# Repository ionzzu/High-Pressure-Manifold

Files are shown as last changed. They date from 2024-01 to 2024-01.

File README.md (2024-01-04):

# High Pressure Manifold

Development of a high pressure manifold to house a miniature VYSZion battery cell at the center.

## Constraints

- Operable to temperatures of 650-800°C and pressures of 10 bar
- Manifold has two inlets and outlets, one each for gas and air
- Design for insertion of temperature probes, pressure sensors, and electrical wires

## Research Paper

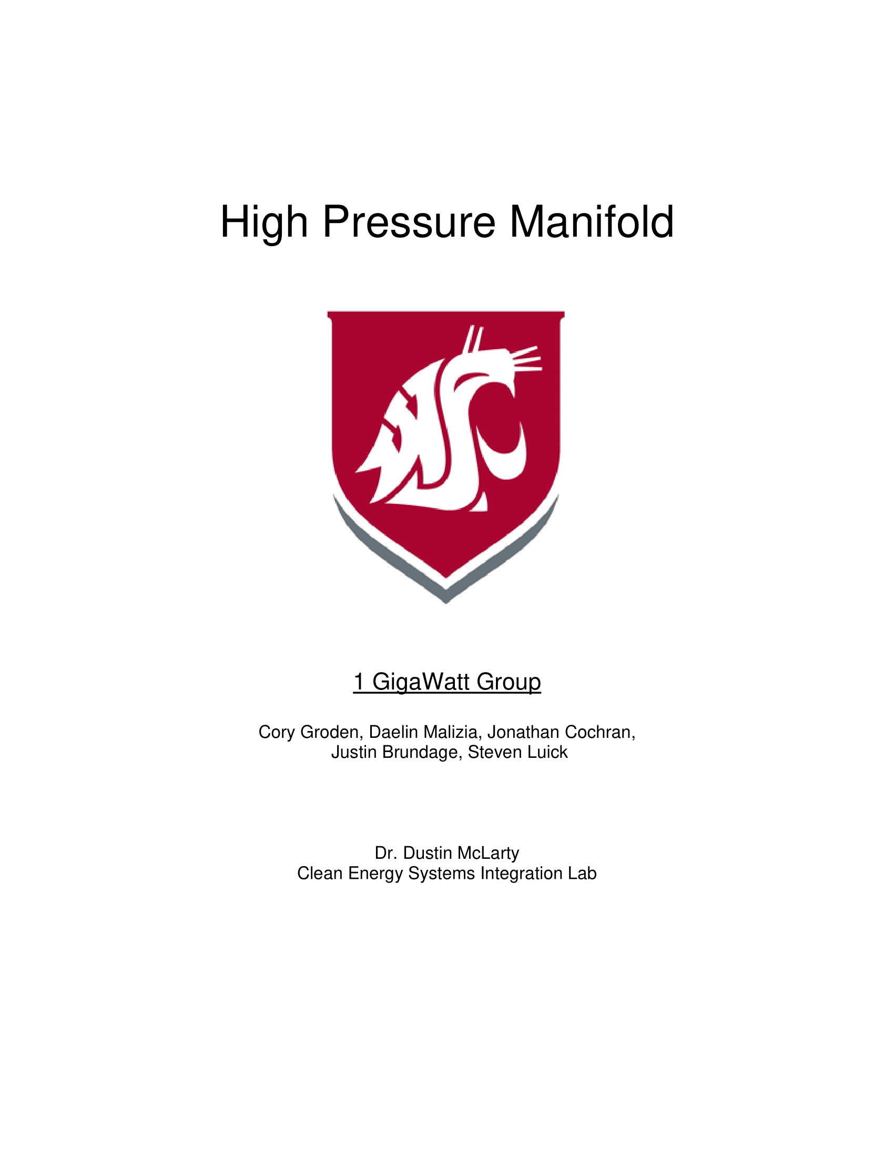
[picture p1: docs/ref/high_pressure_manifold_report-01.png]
report-01


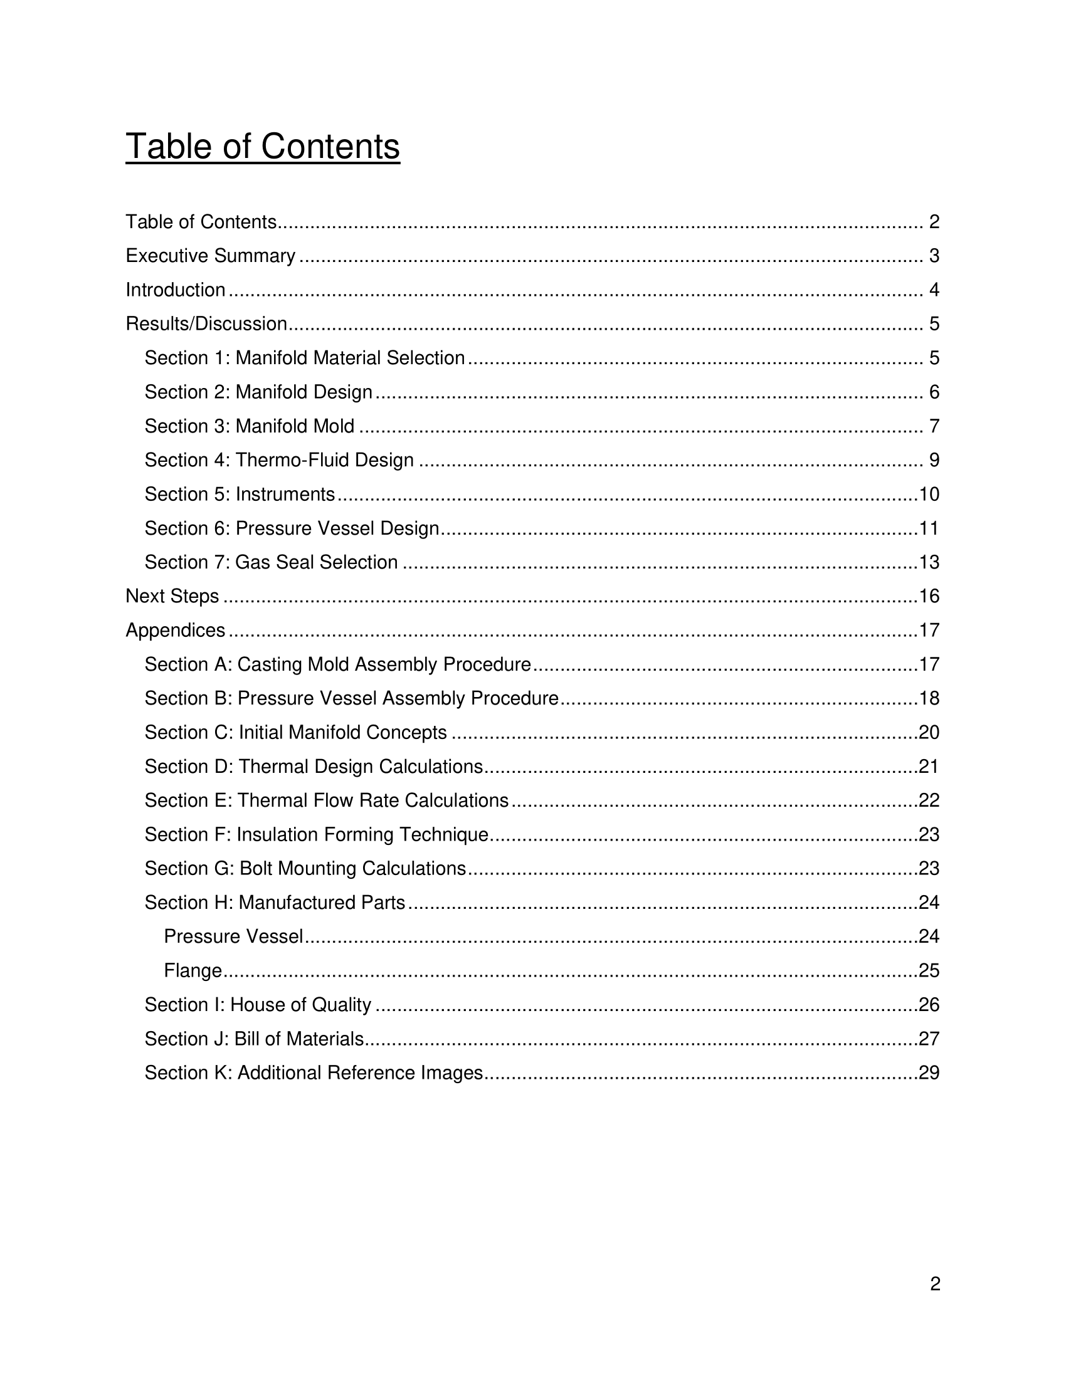
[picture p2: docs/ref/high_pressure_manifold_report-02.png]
report-02


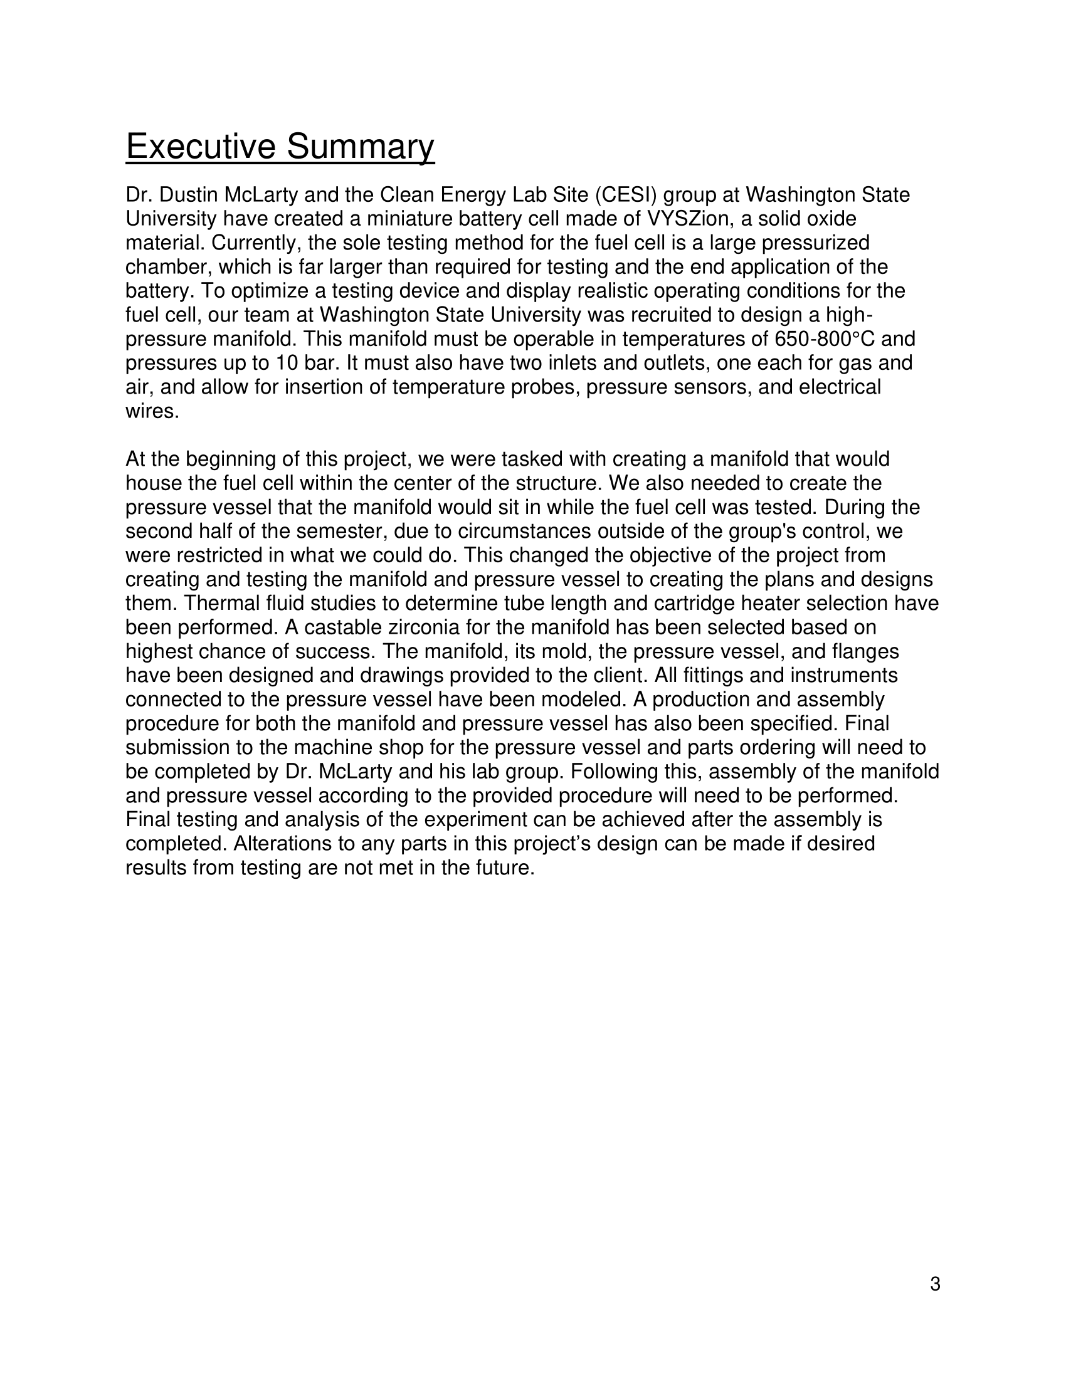
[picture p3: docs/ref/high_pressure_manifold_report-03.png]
report-03


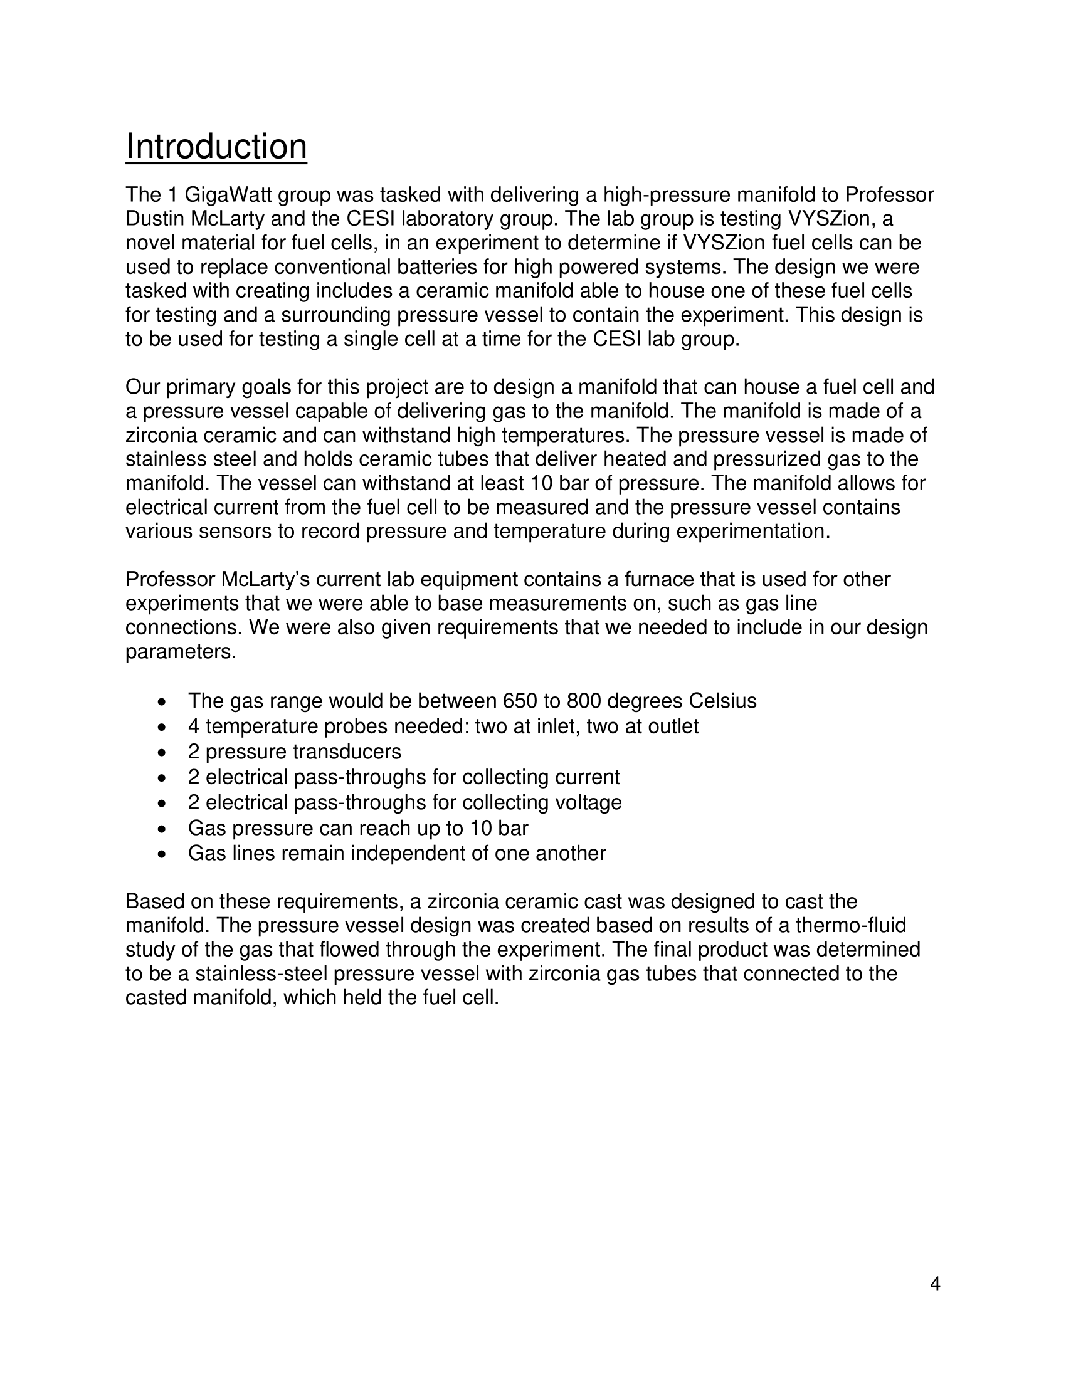
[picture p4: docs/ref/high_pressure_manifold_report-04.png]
report-04


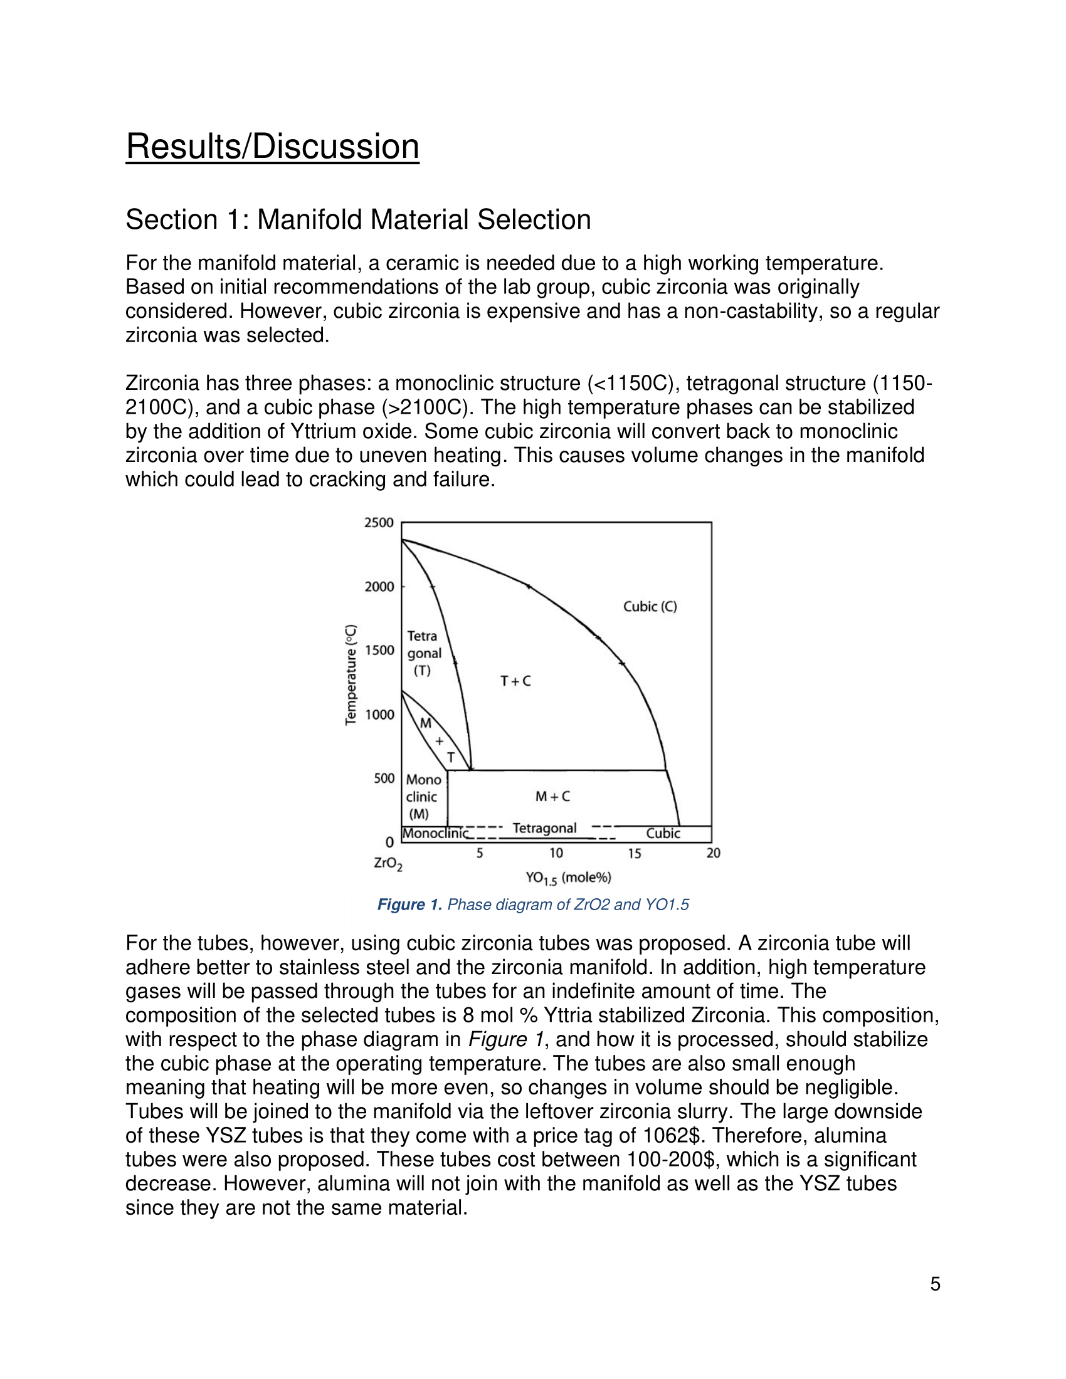
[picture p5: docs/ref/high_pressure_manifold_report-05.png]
report-05


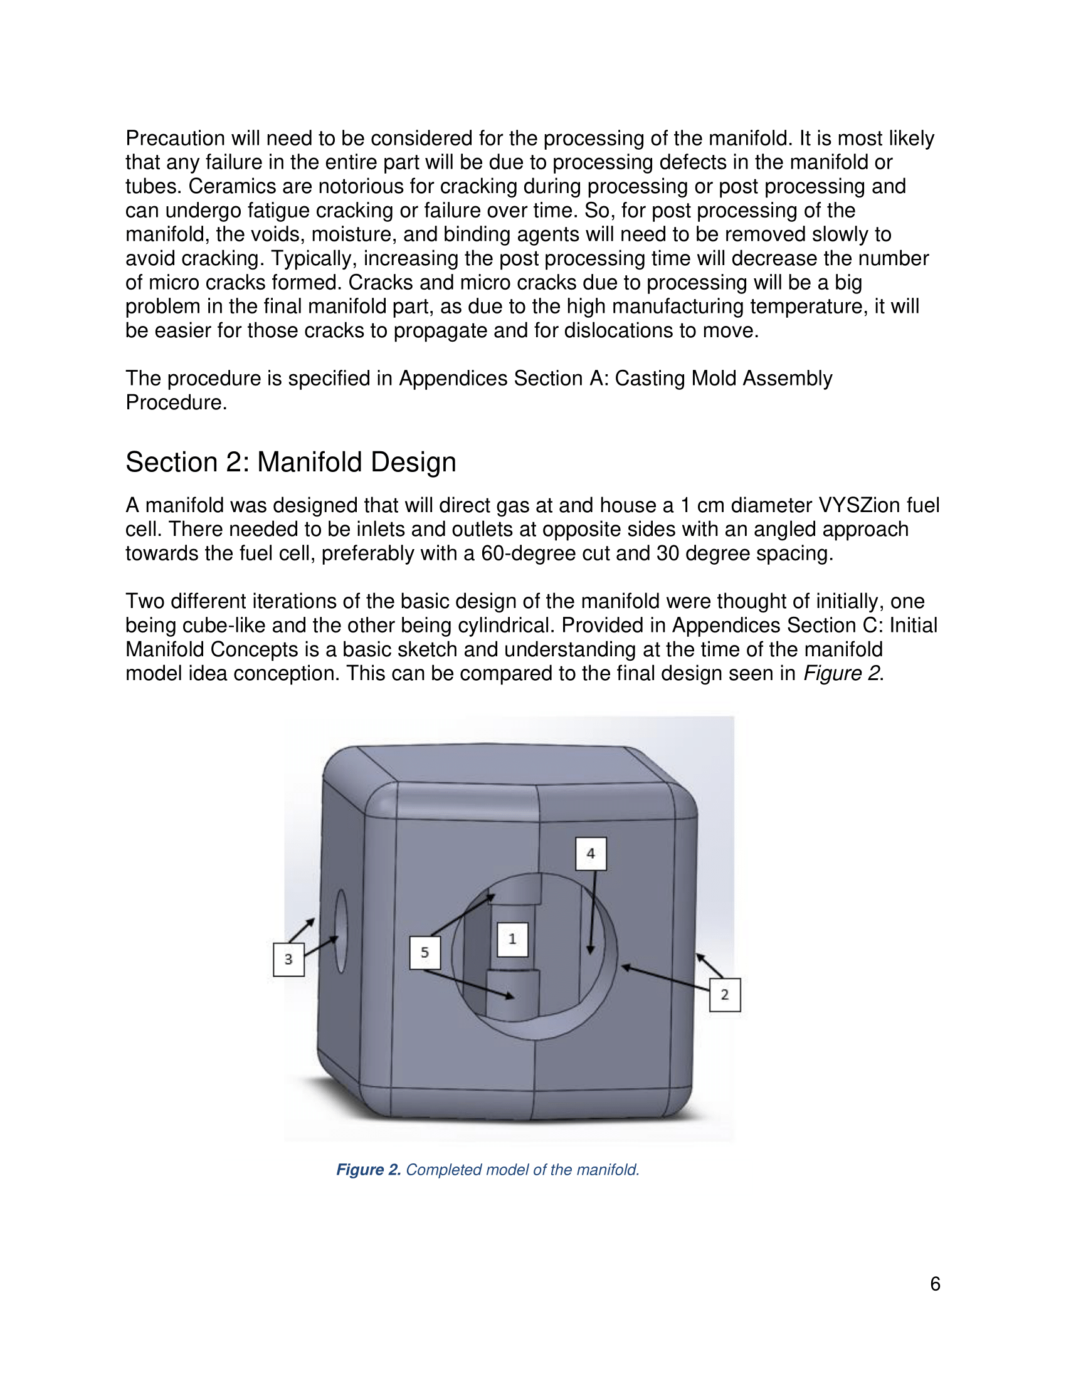
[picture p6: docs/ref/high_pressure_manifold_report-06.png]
report-06


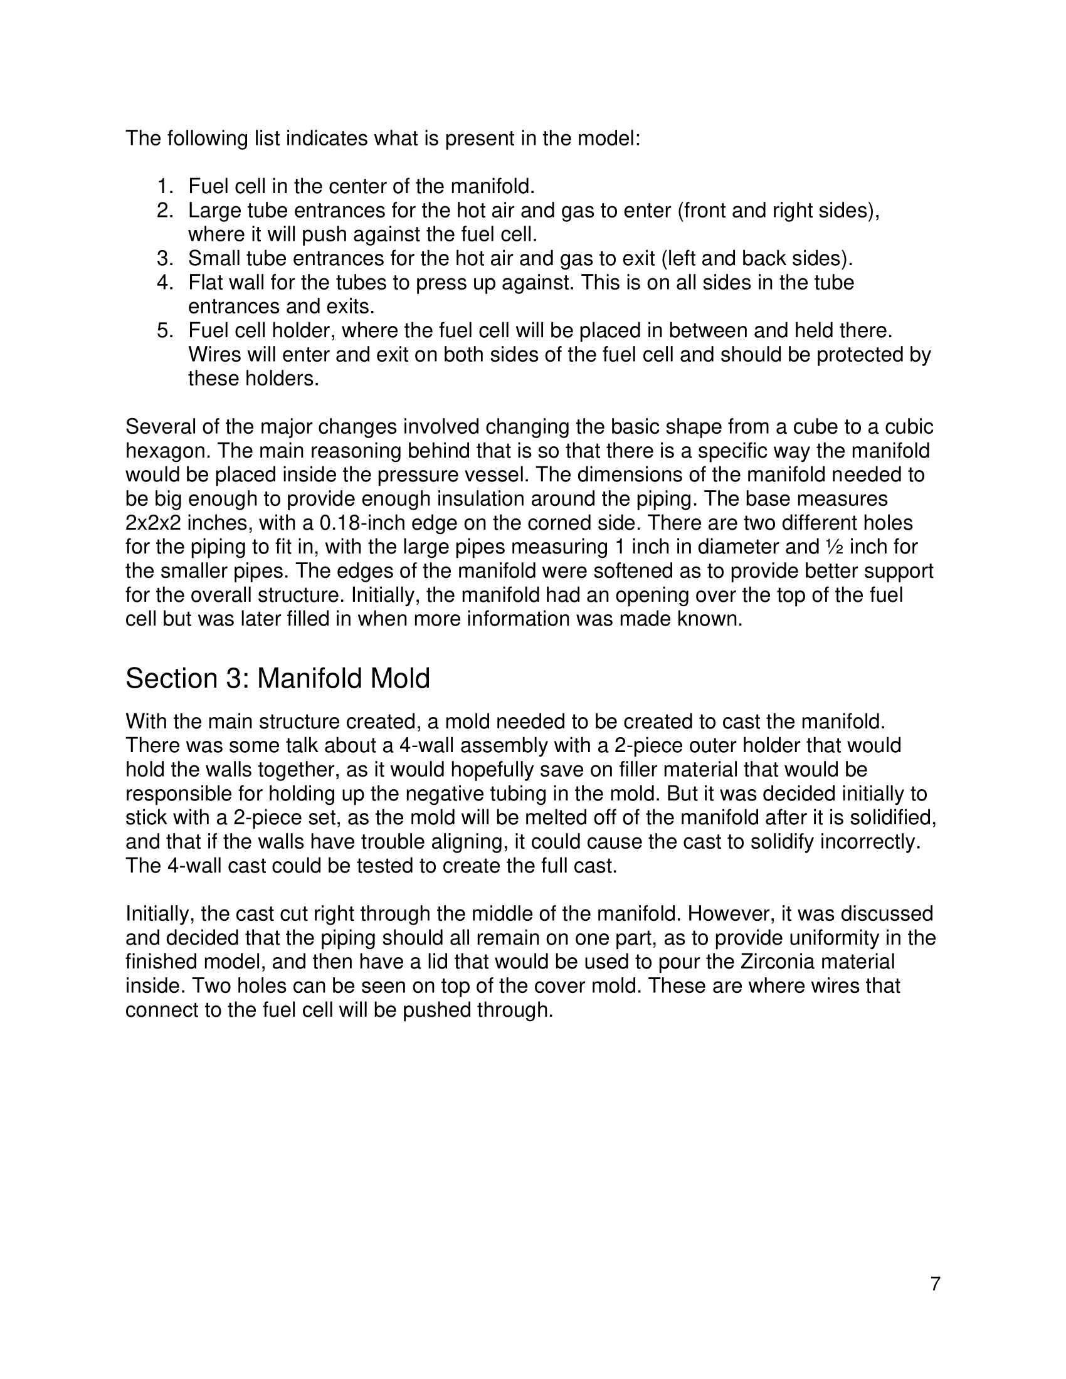
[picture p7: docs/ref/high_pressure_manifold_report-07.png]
report-07


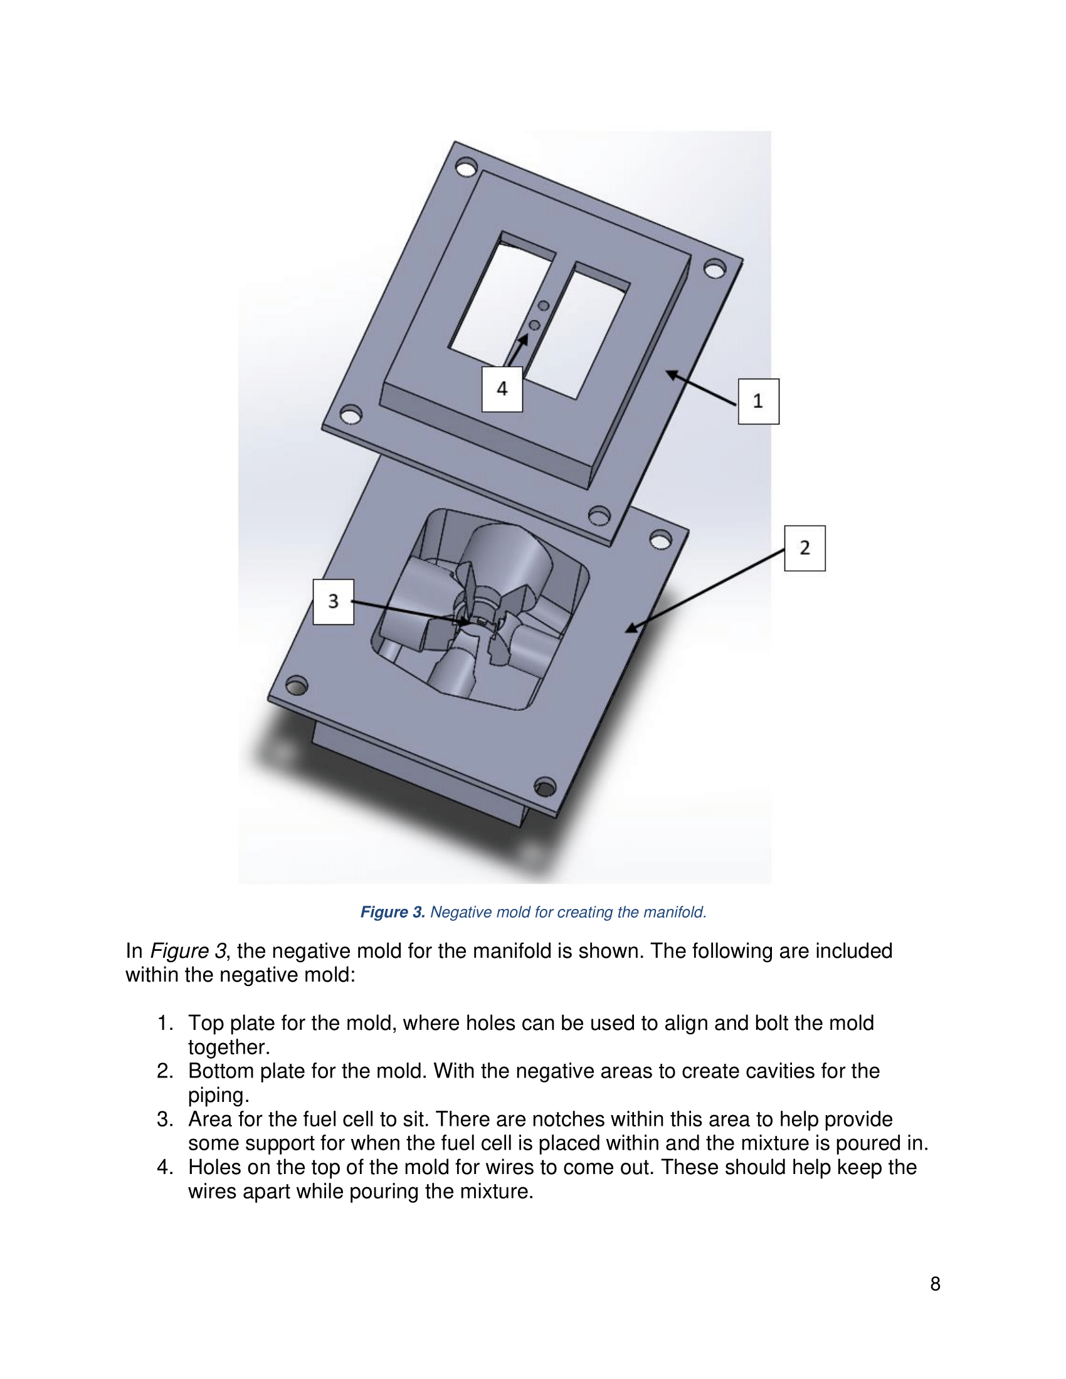
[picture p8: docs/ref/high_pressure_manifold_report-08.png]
report-08


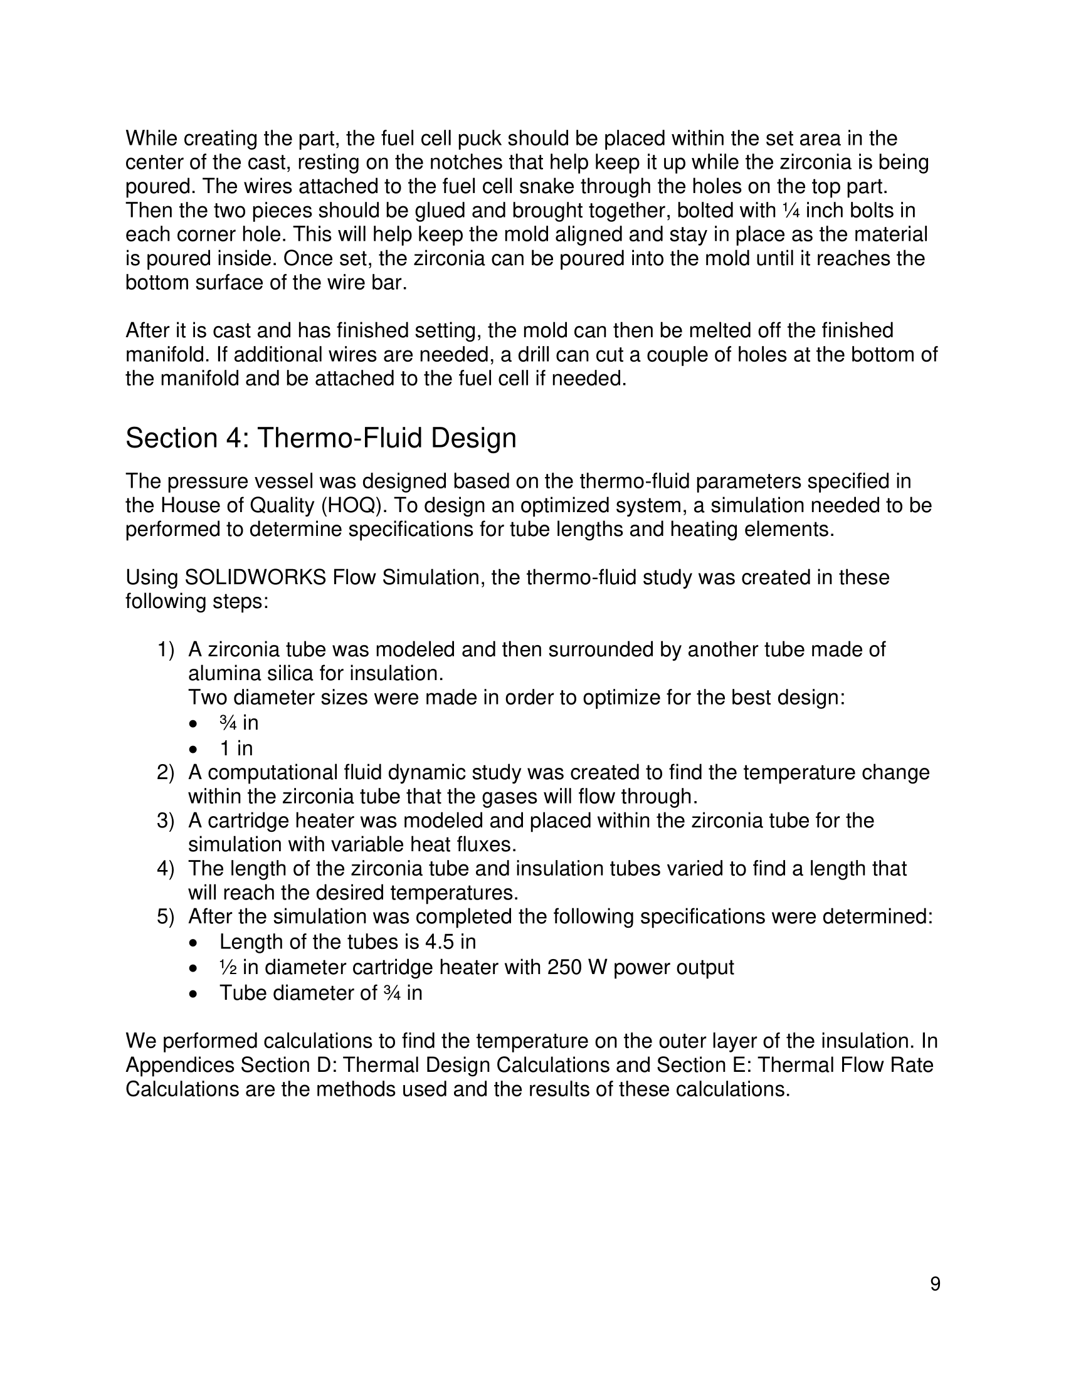
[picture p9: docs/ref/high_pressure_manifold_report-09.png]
report-09


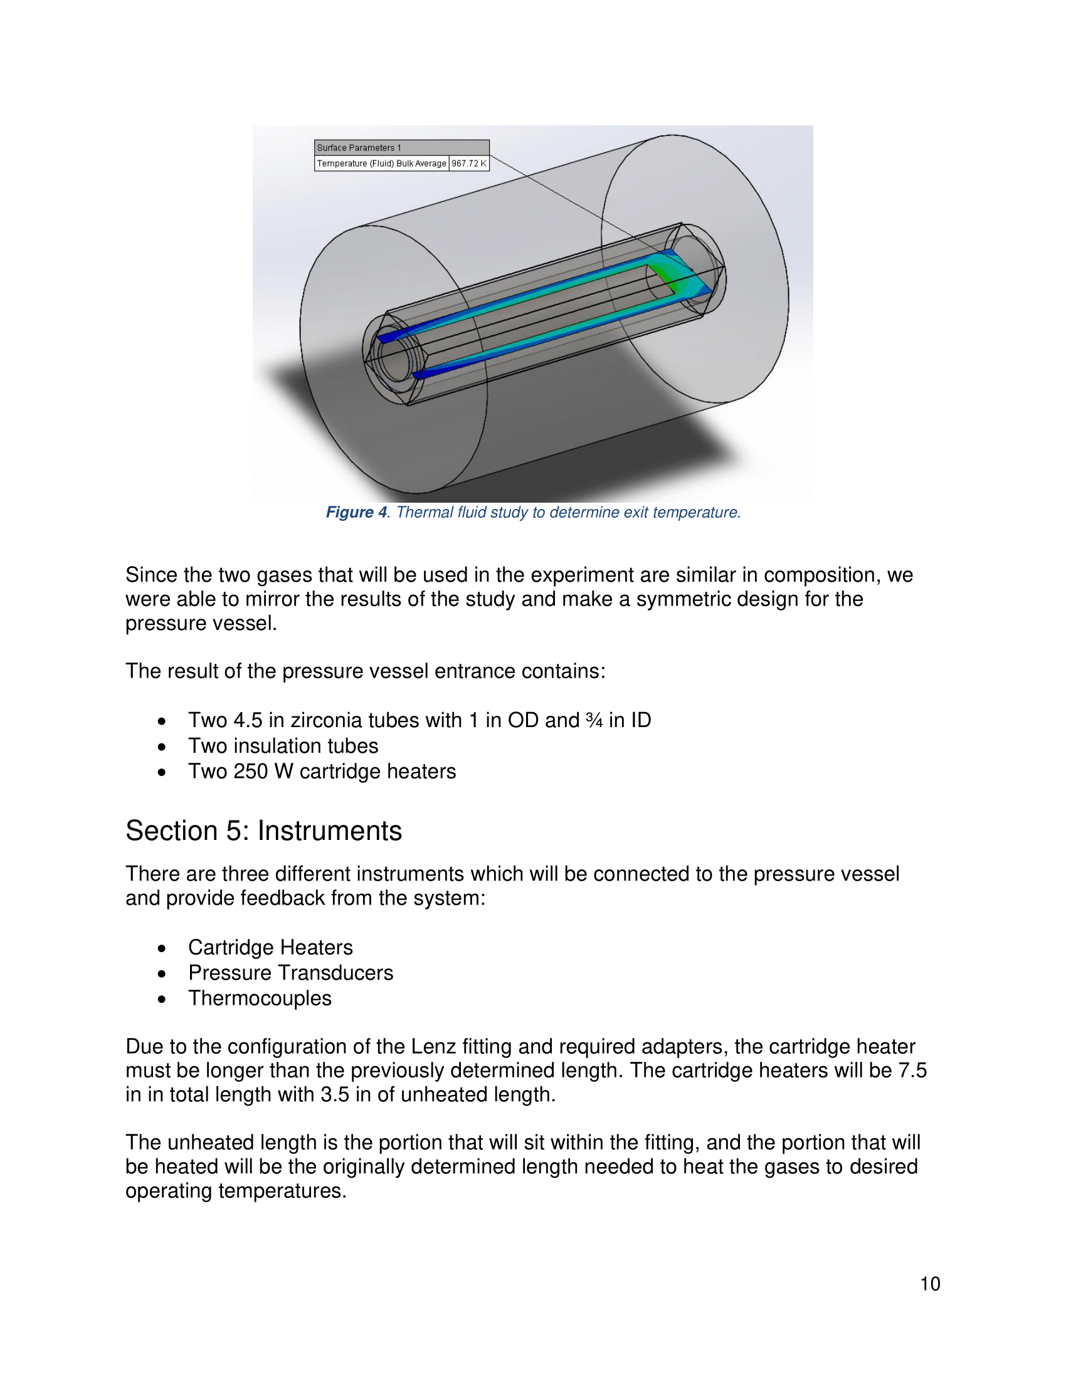
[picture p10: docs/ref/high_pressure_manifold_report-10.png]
report-10


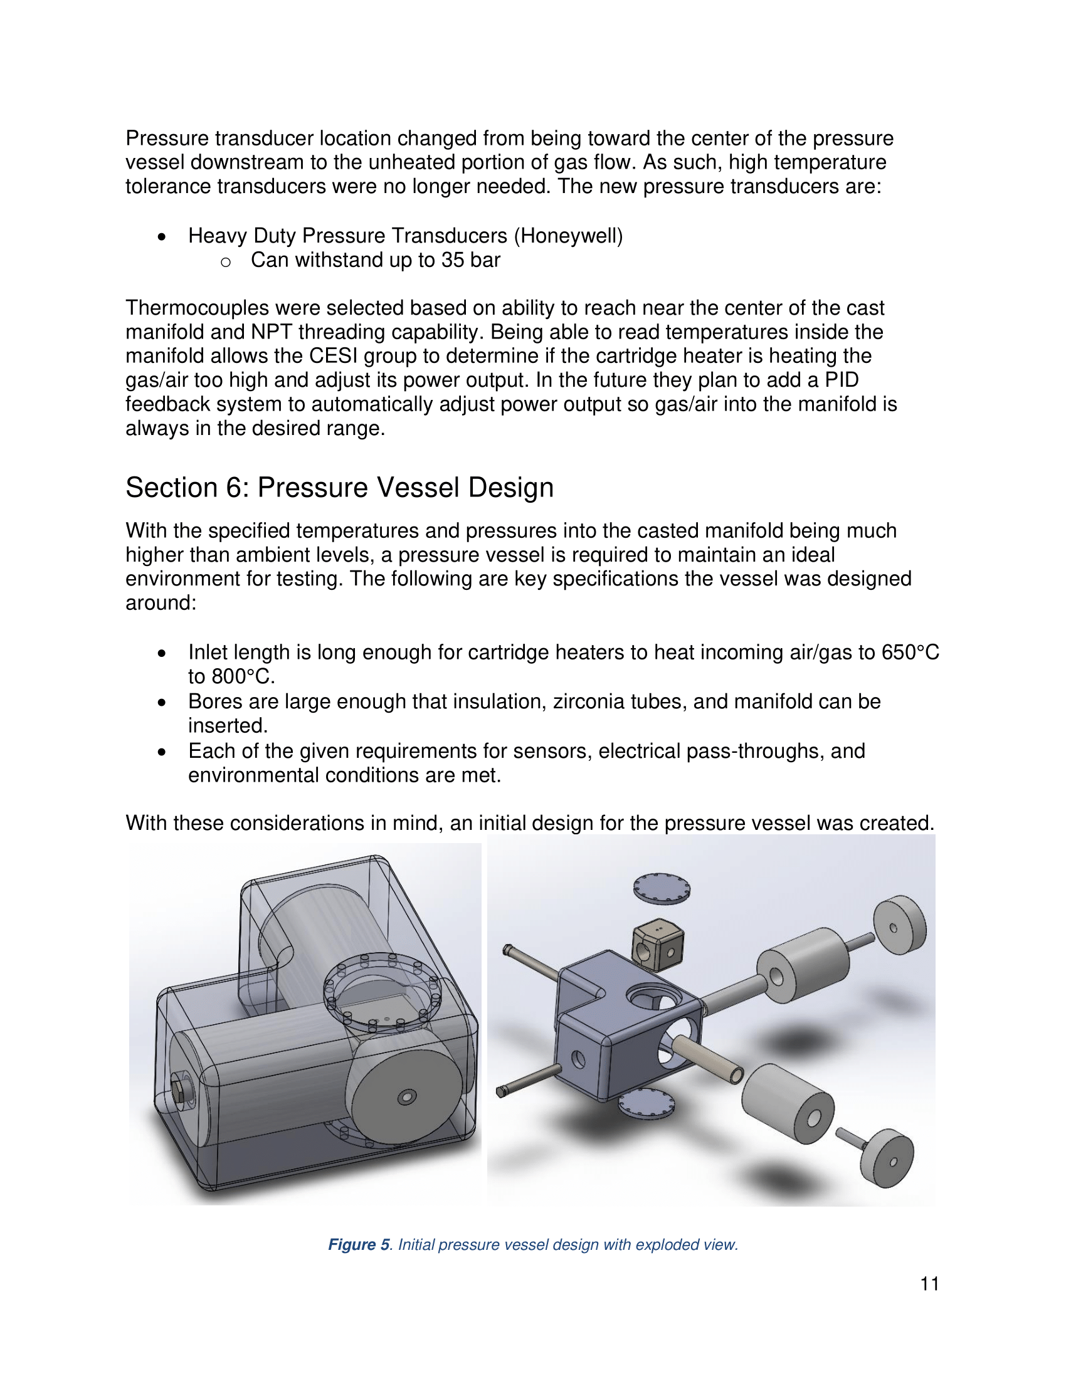
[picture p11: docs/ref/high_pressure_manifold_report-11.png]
report-11


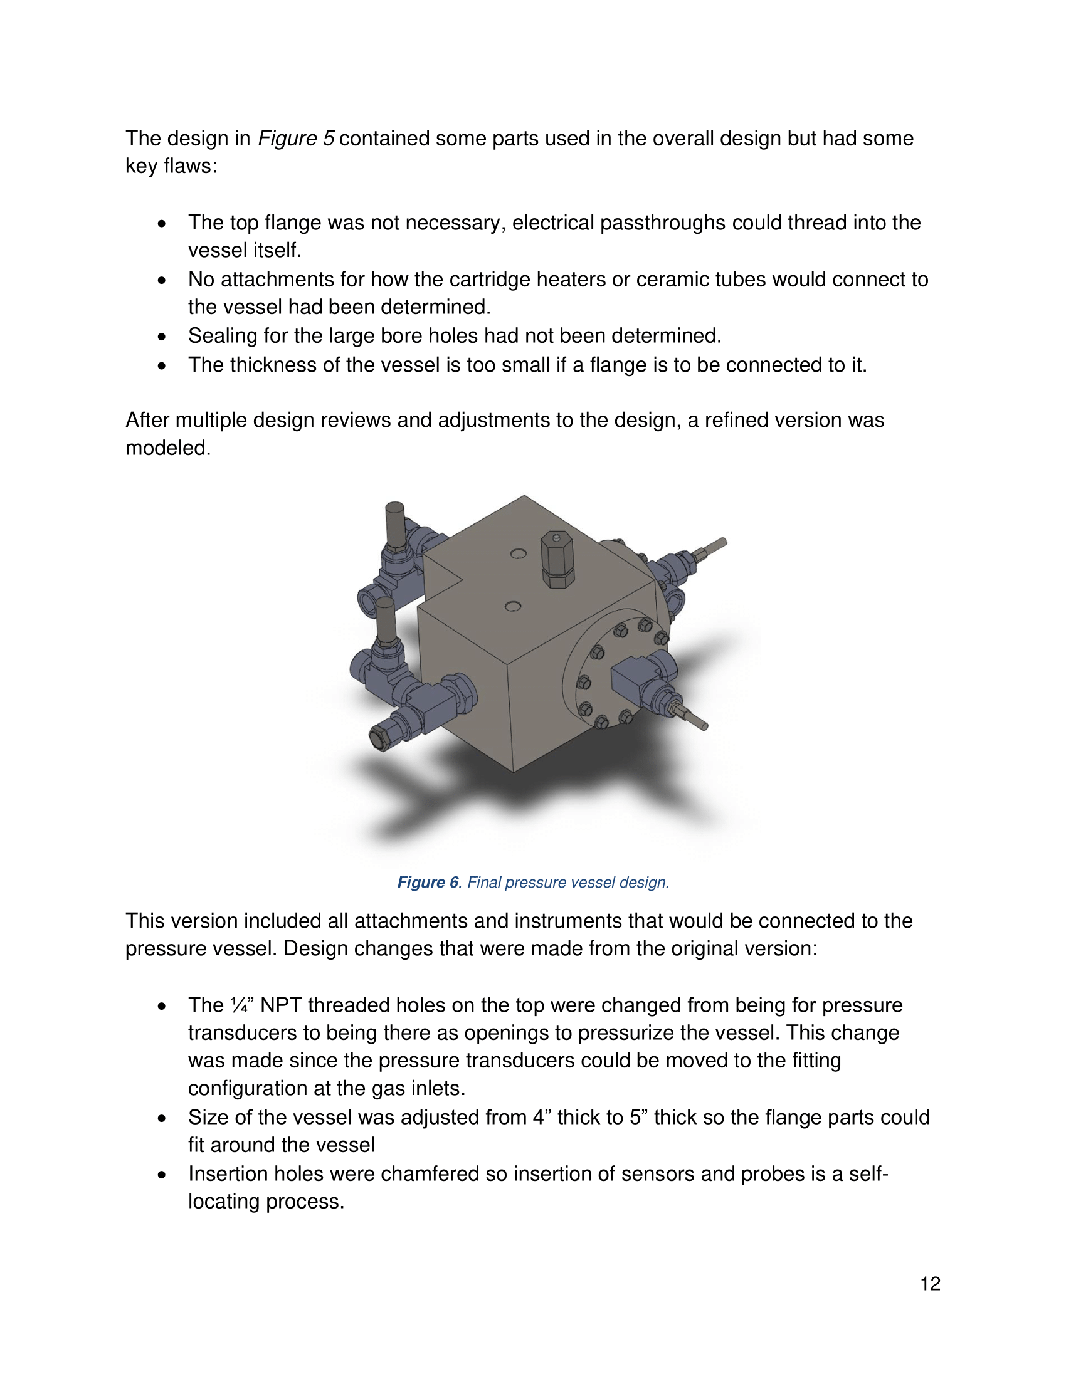
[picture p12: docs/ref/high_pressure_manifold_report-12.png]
report-12


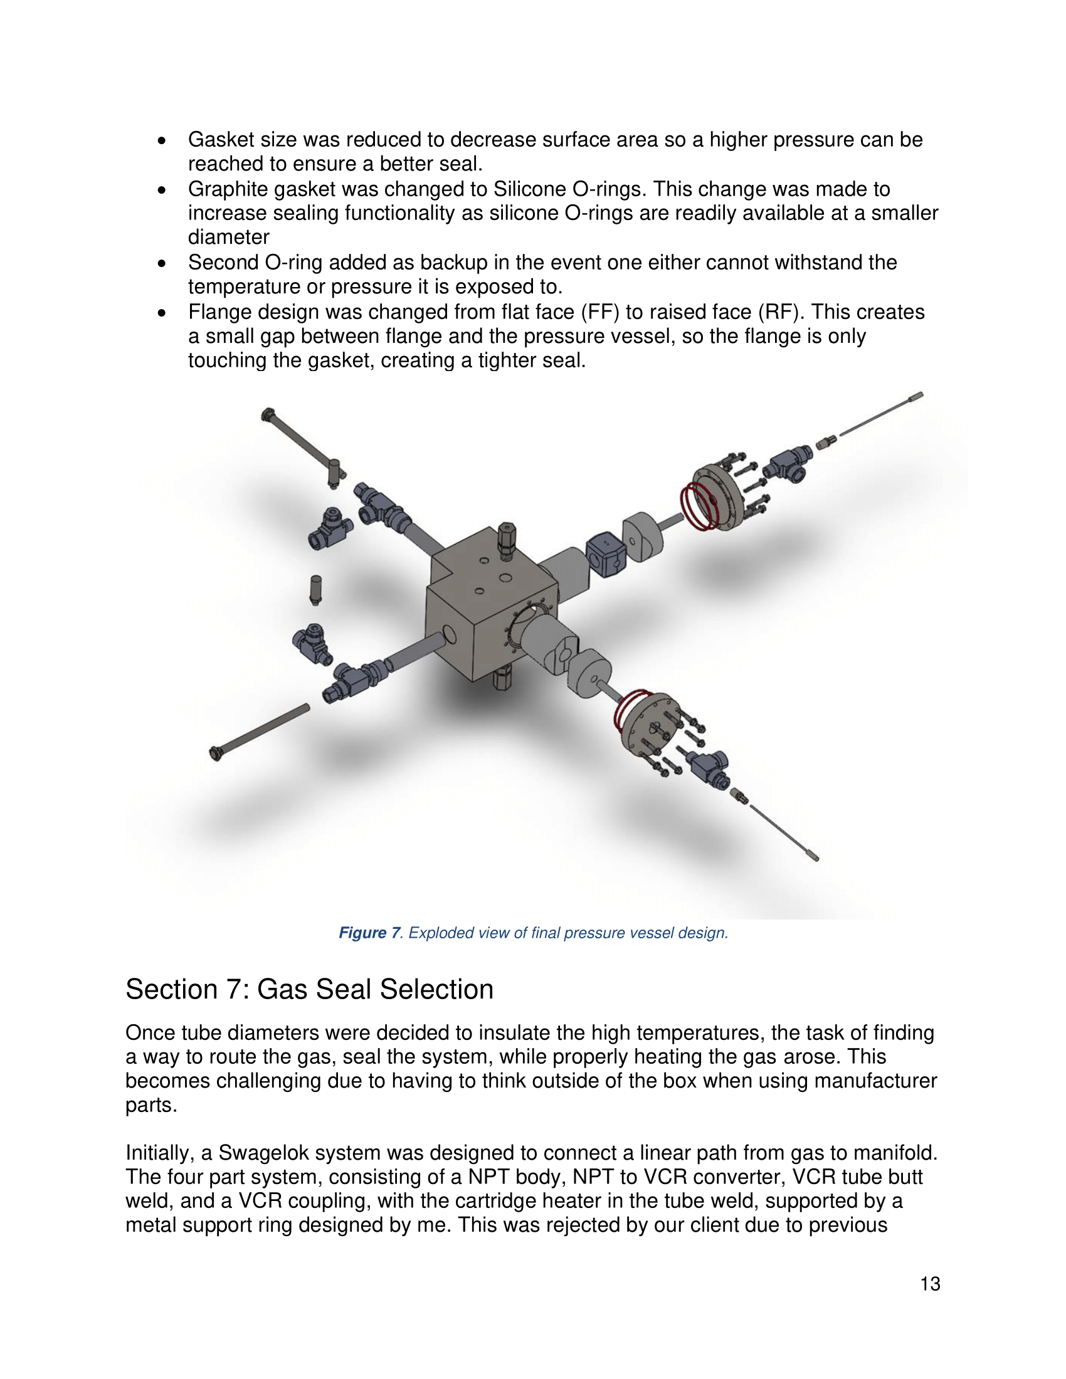
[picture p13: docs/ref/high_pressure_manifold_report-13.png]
report-13


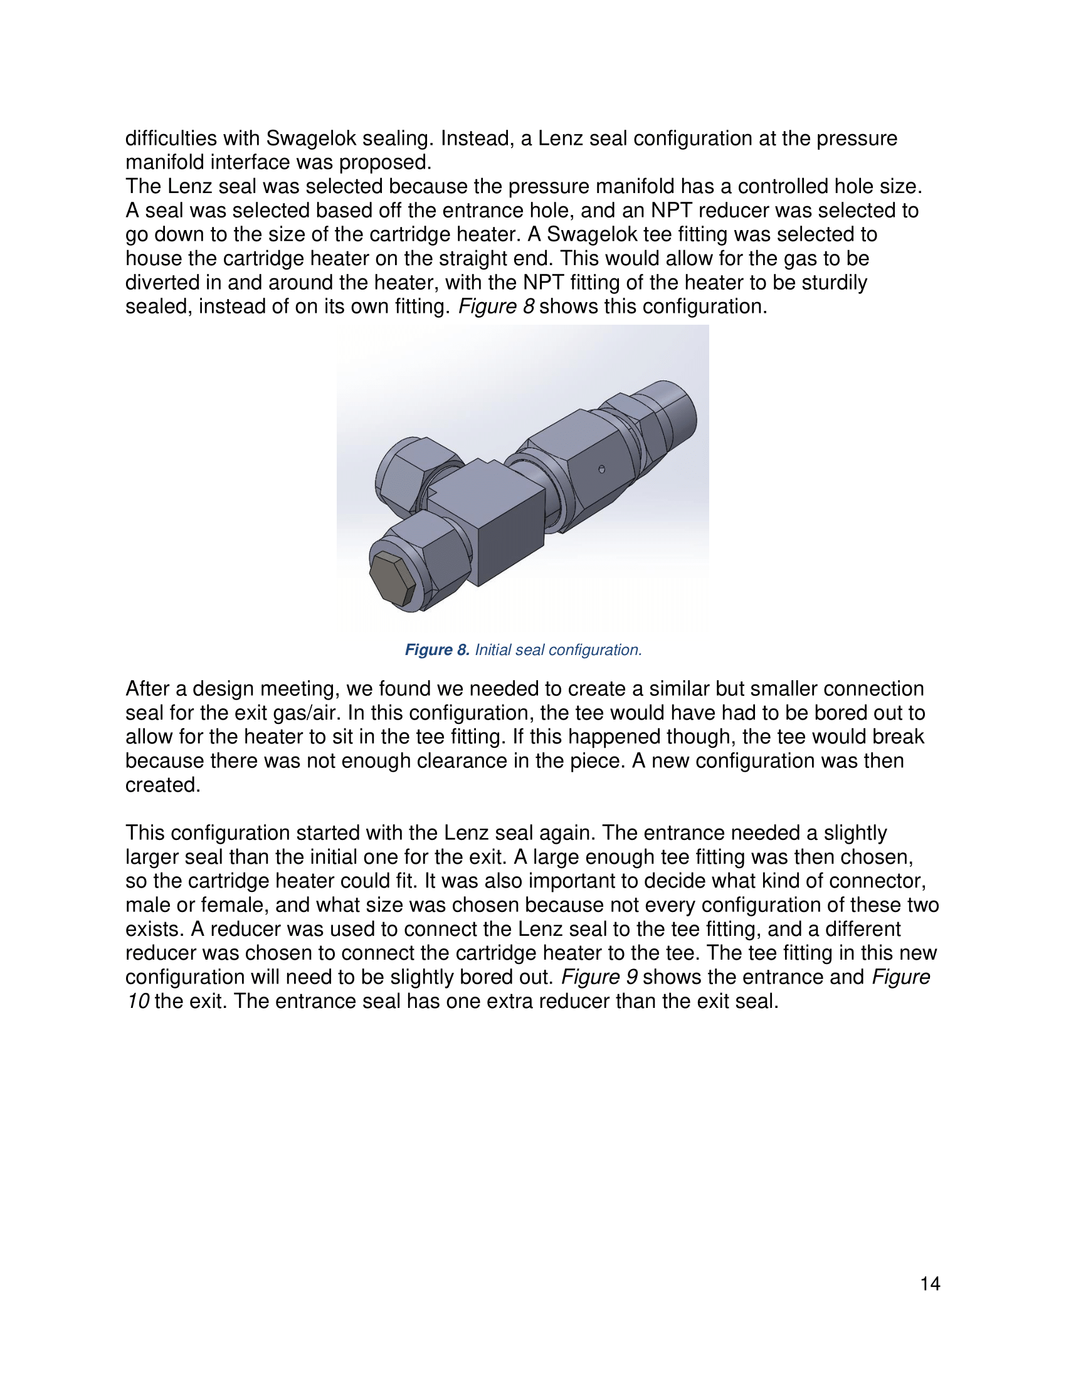
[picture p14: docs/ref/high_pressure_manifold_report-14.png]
report-14


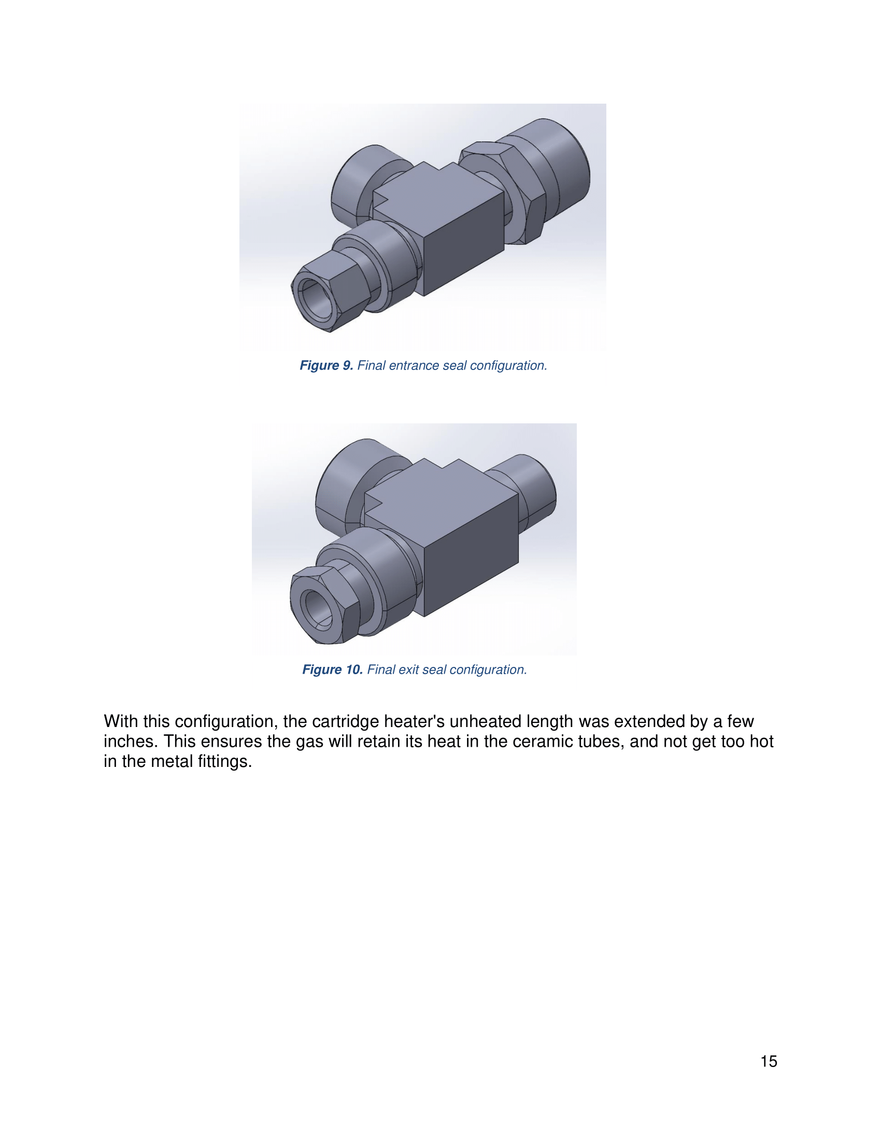
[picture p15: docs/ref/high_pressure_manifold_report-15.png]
report-15


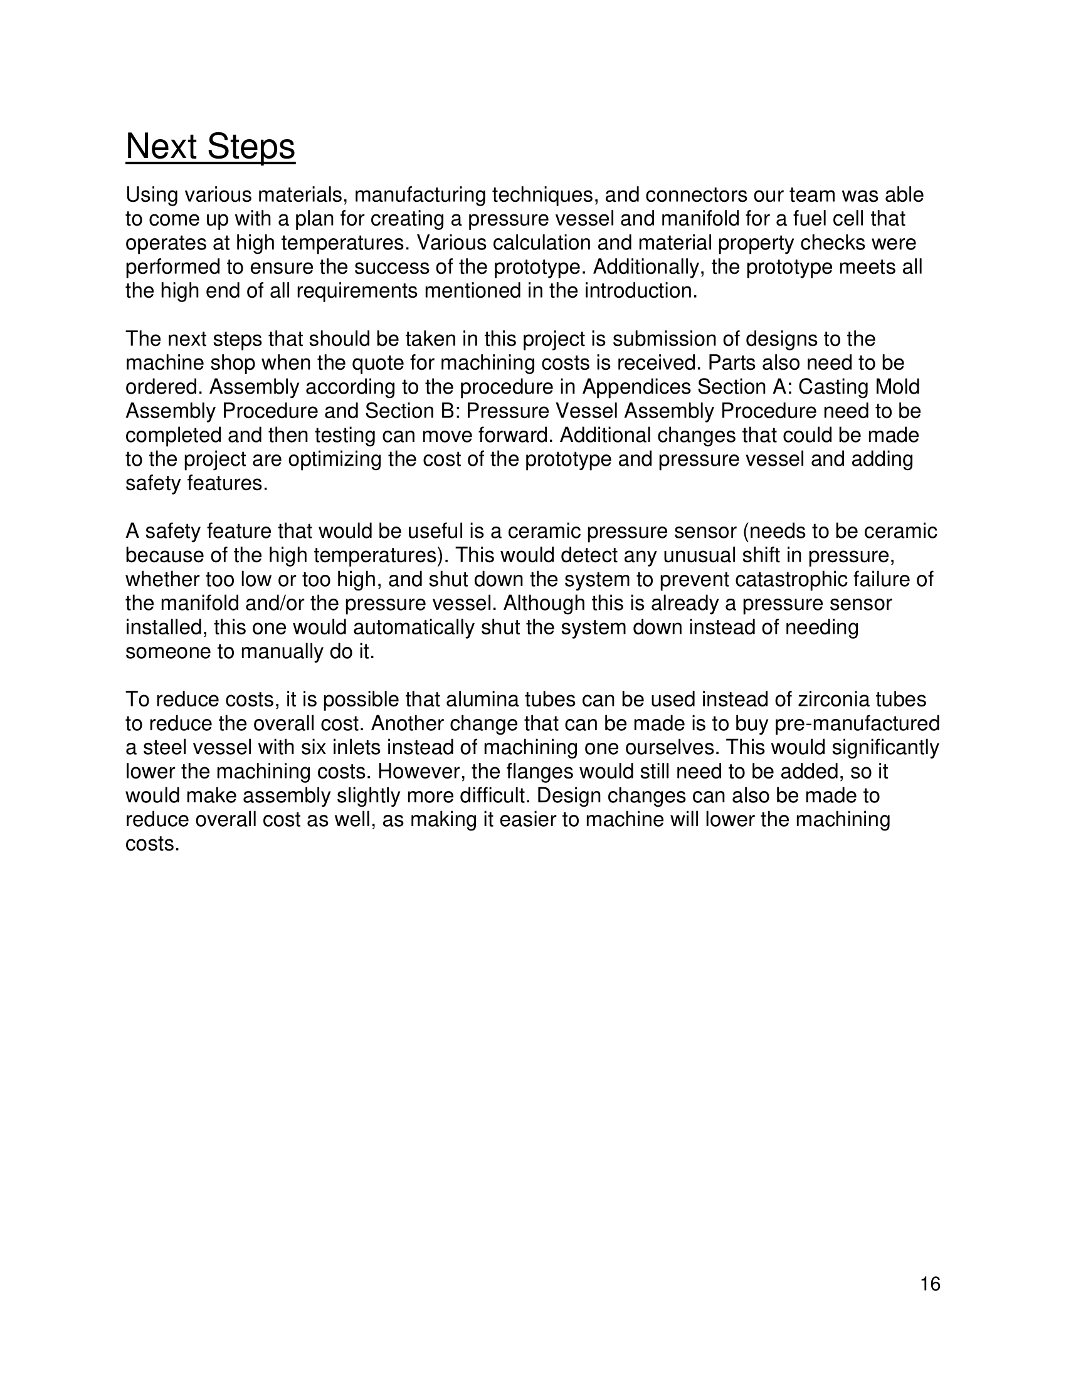
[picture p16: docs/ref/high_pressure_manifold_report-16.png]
report-16


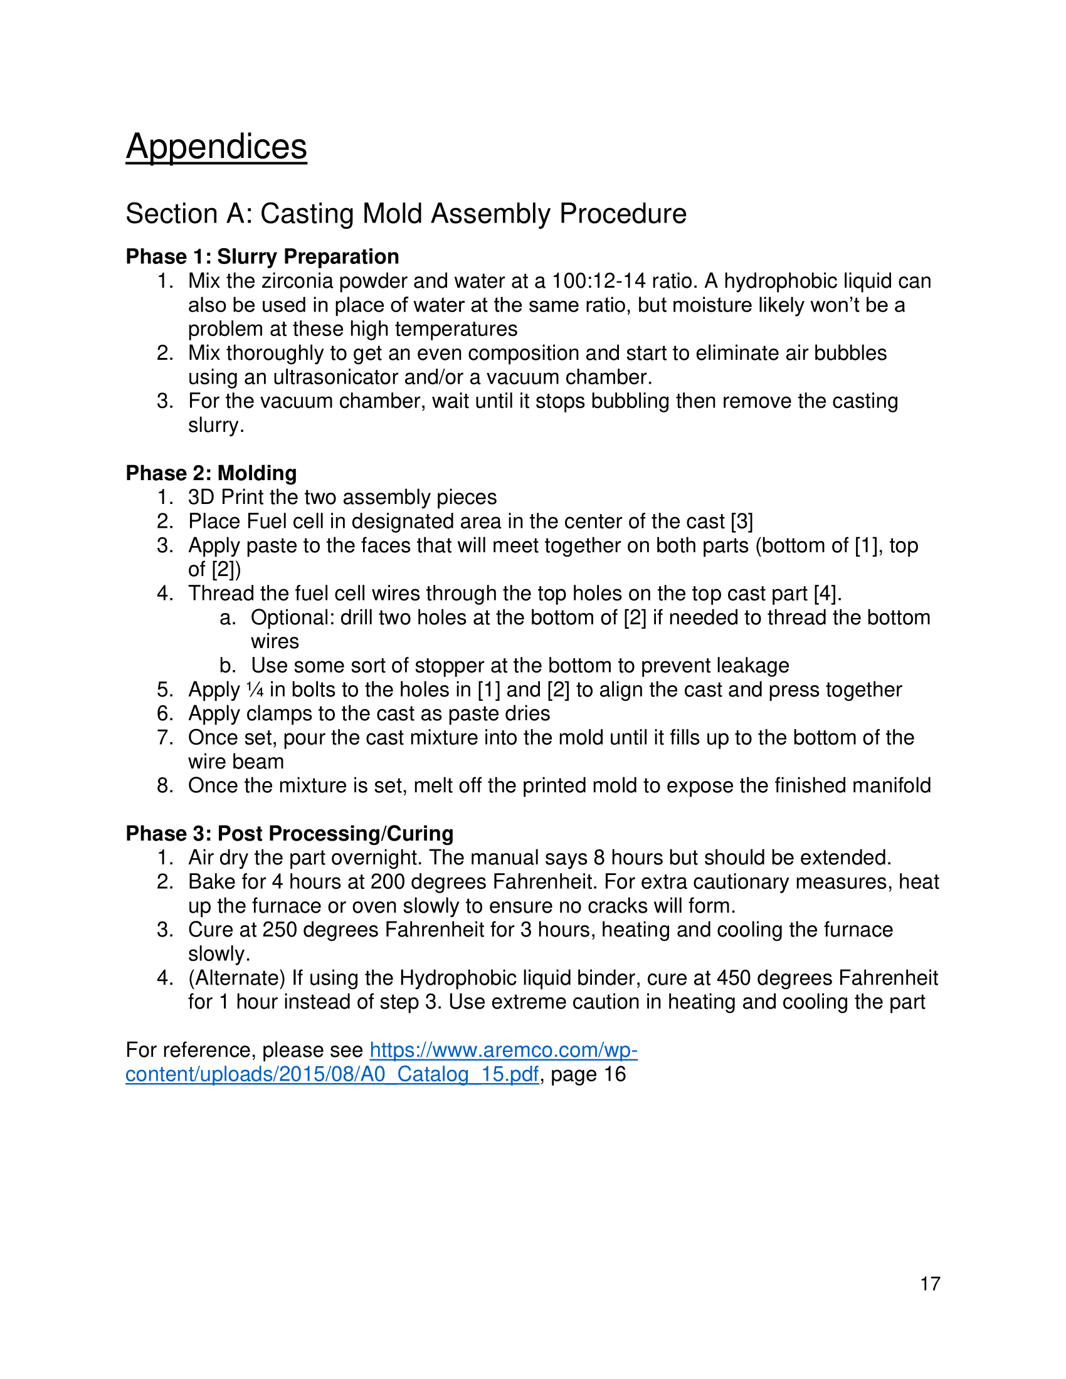
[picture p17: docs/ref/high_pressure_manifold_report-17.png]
report-17


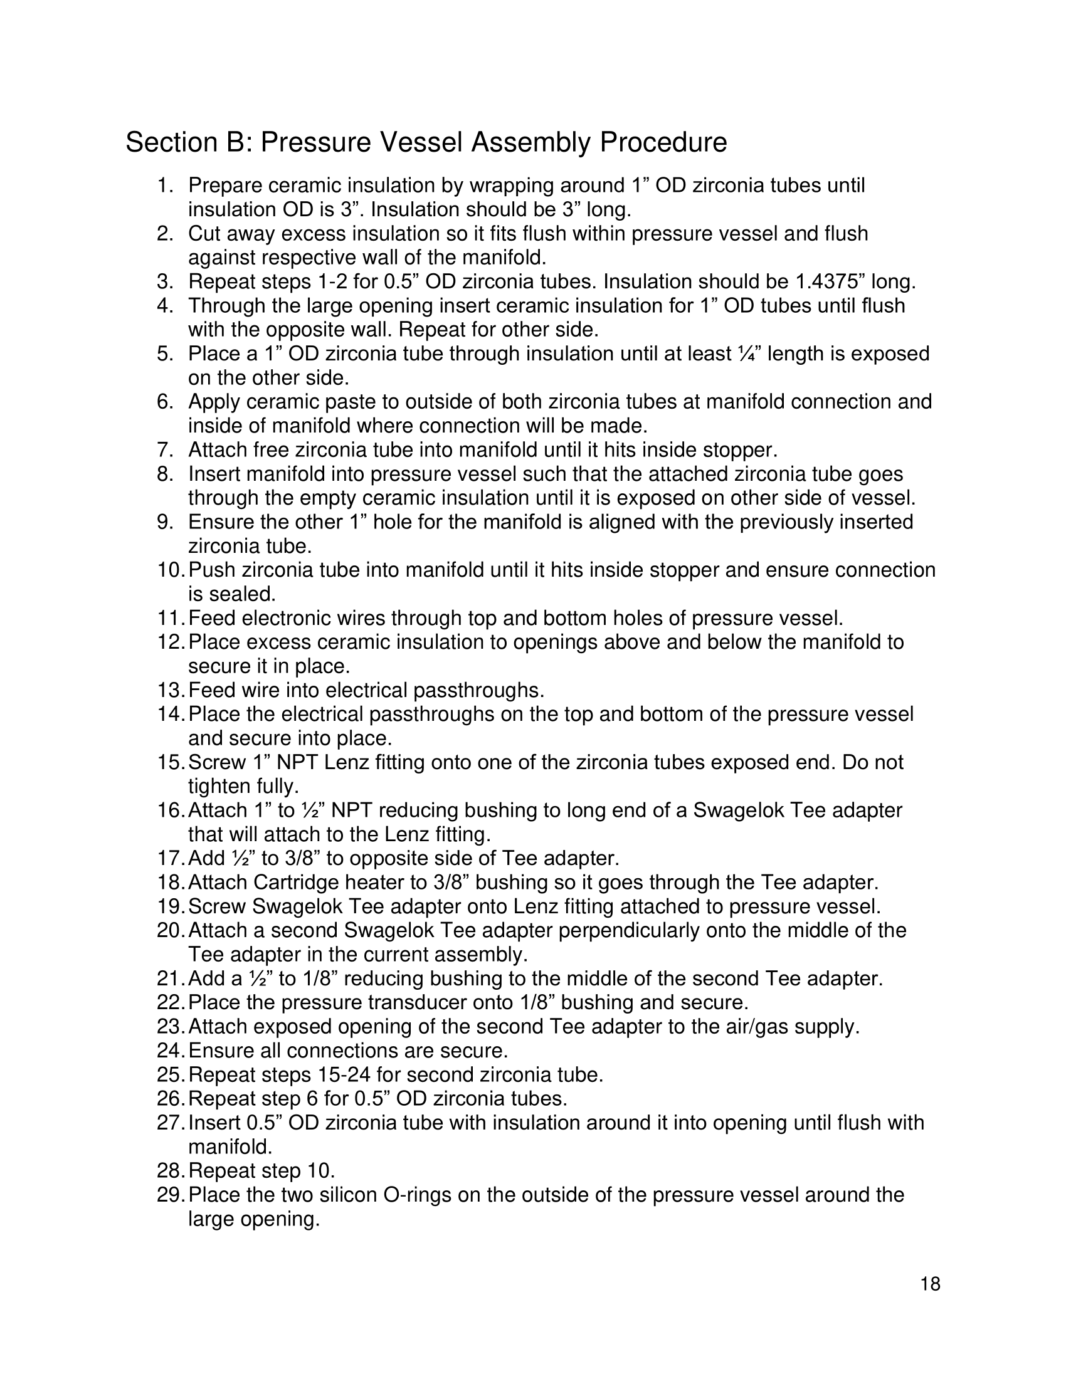
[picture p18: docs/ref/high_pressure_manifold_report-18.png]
report-18


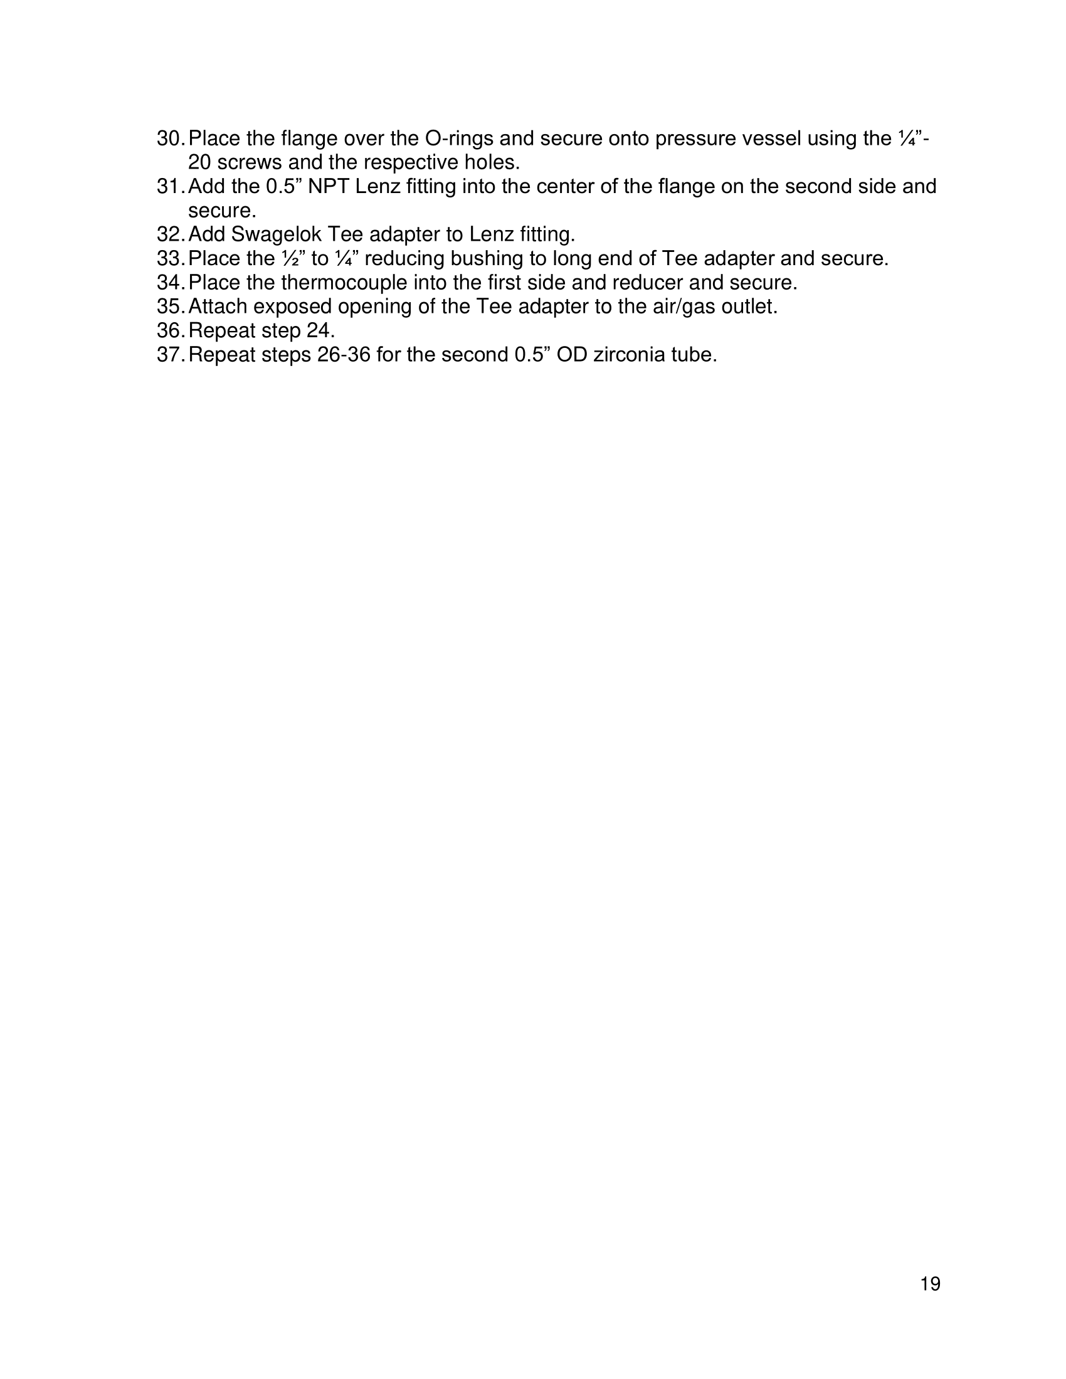
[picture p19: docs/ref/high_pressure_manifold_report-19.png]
report-19


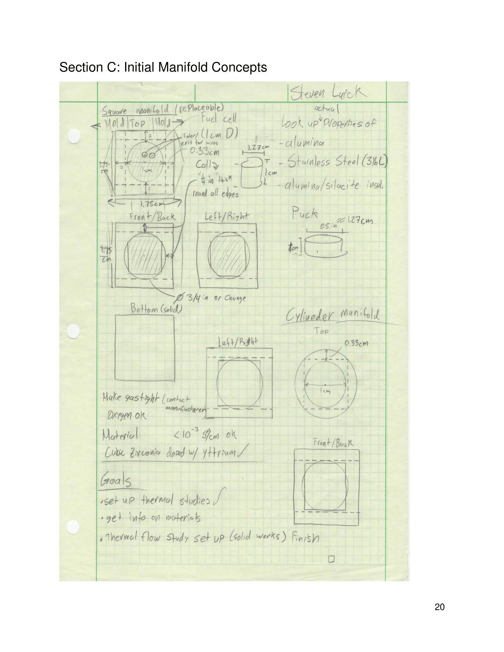
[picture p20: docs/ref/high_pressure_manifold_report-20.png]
report-20


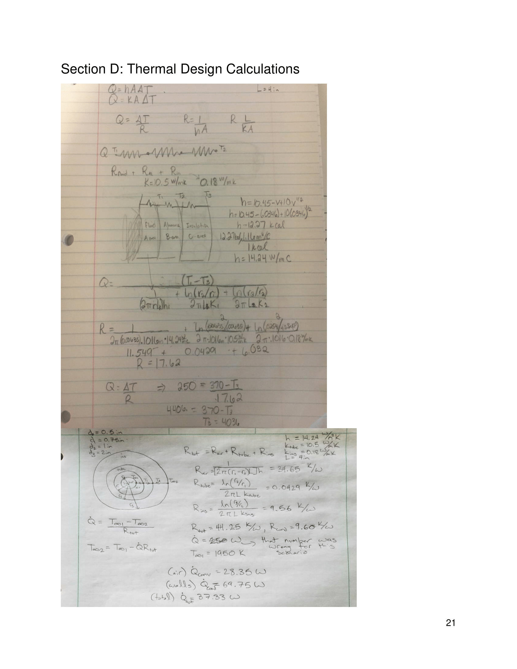
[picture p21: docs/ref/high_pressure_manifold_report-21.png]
report-21


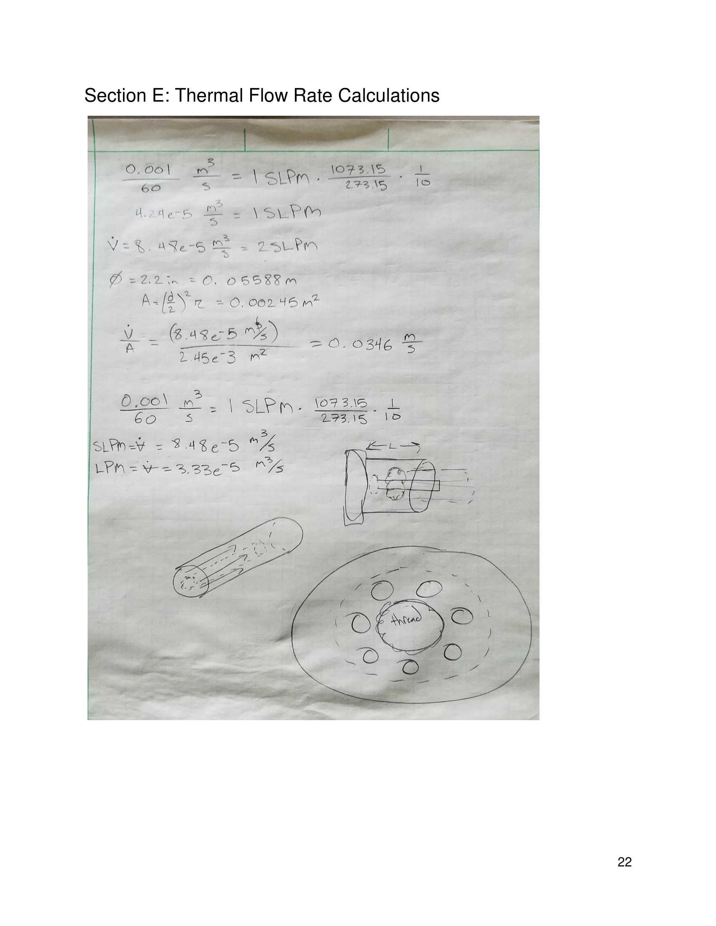
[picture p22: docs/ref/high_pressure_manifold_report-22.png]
report-22


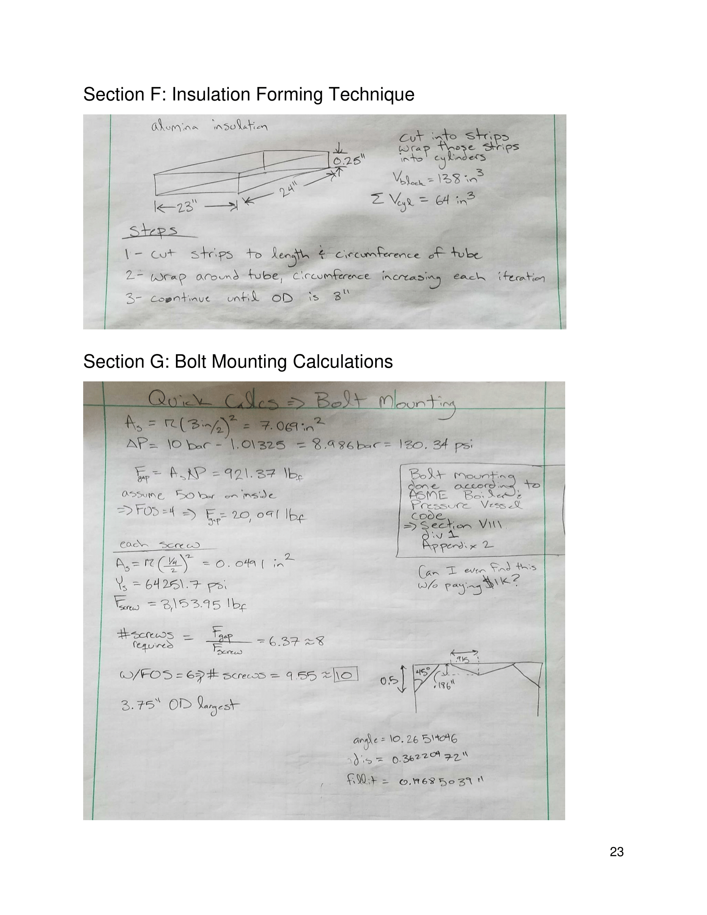
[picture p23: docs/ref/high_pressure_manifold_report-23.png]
report-23


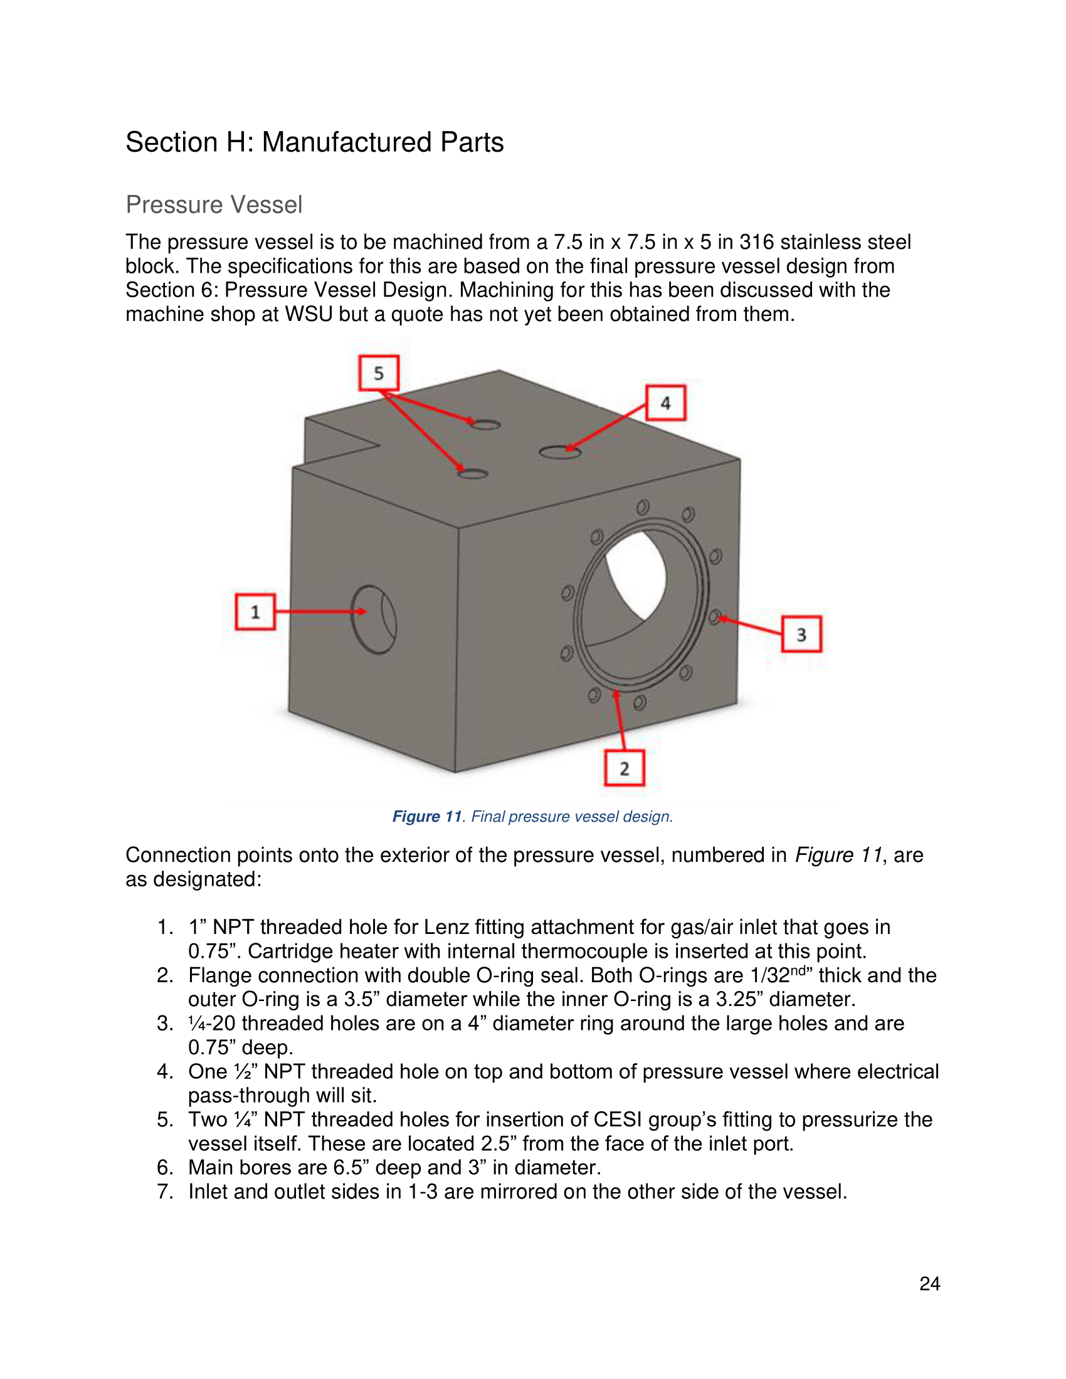
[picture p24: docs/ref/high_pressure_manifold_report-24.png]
report-24


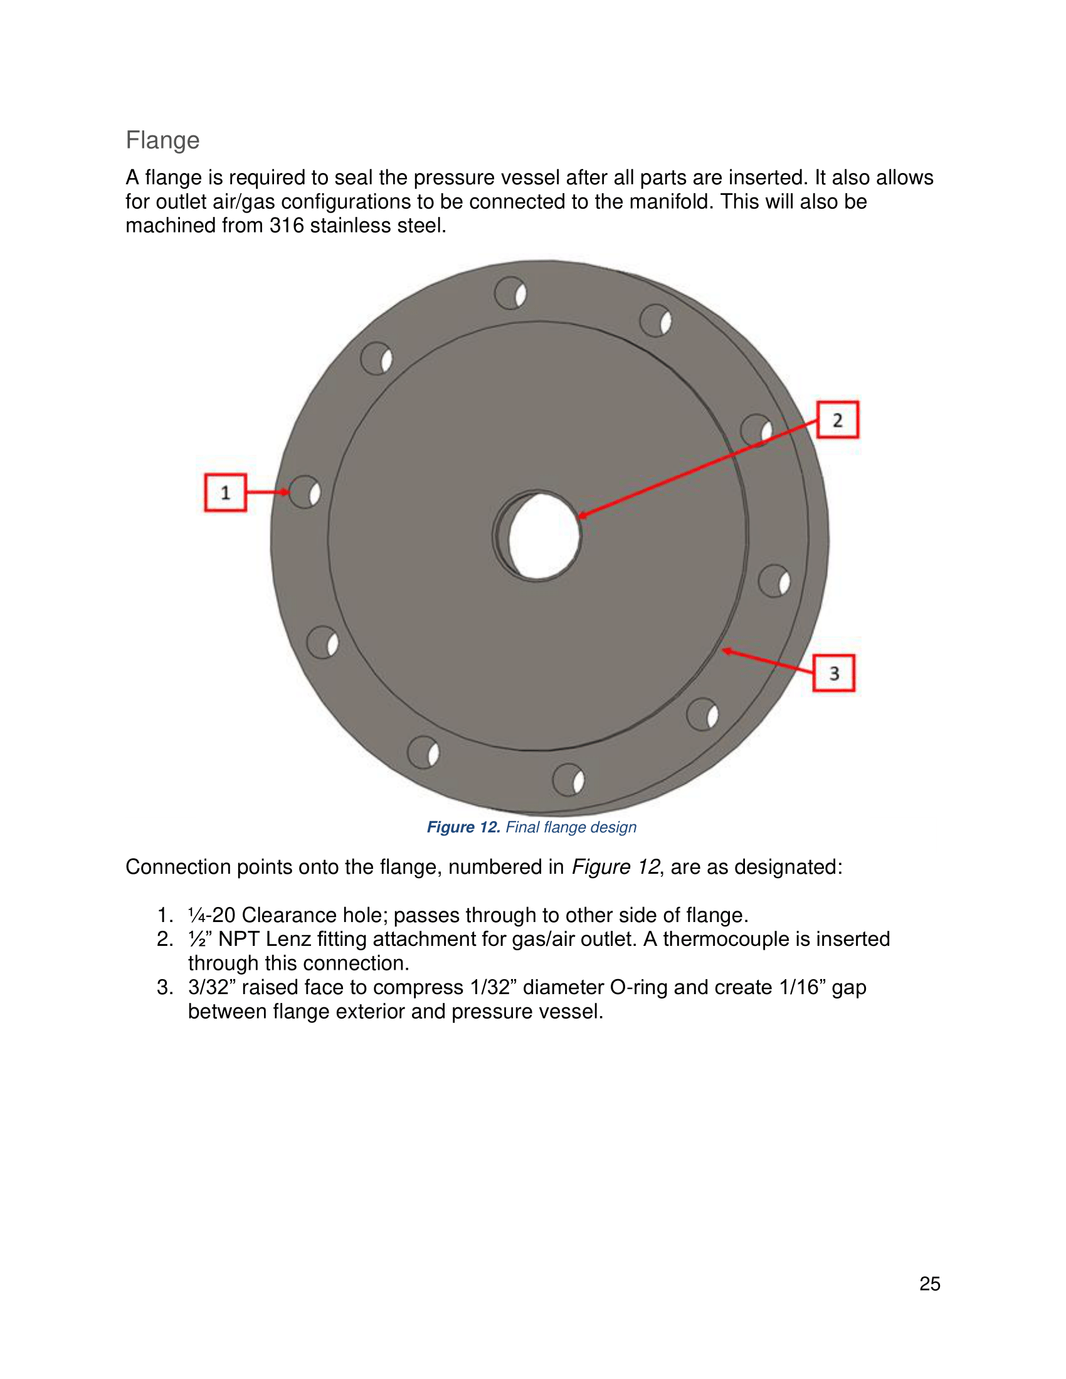
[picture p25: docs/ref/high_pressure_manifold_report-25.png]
report-25


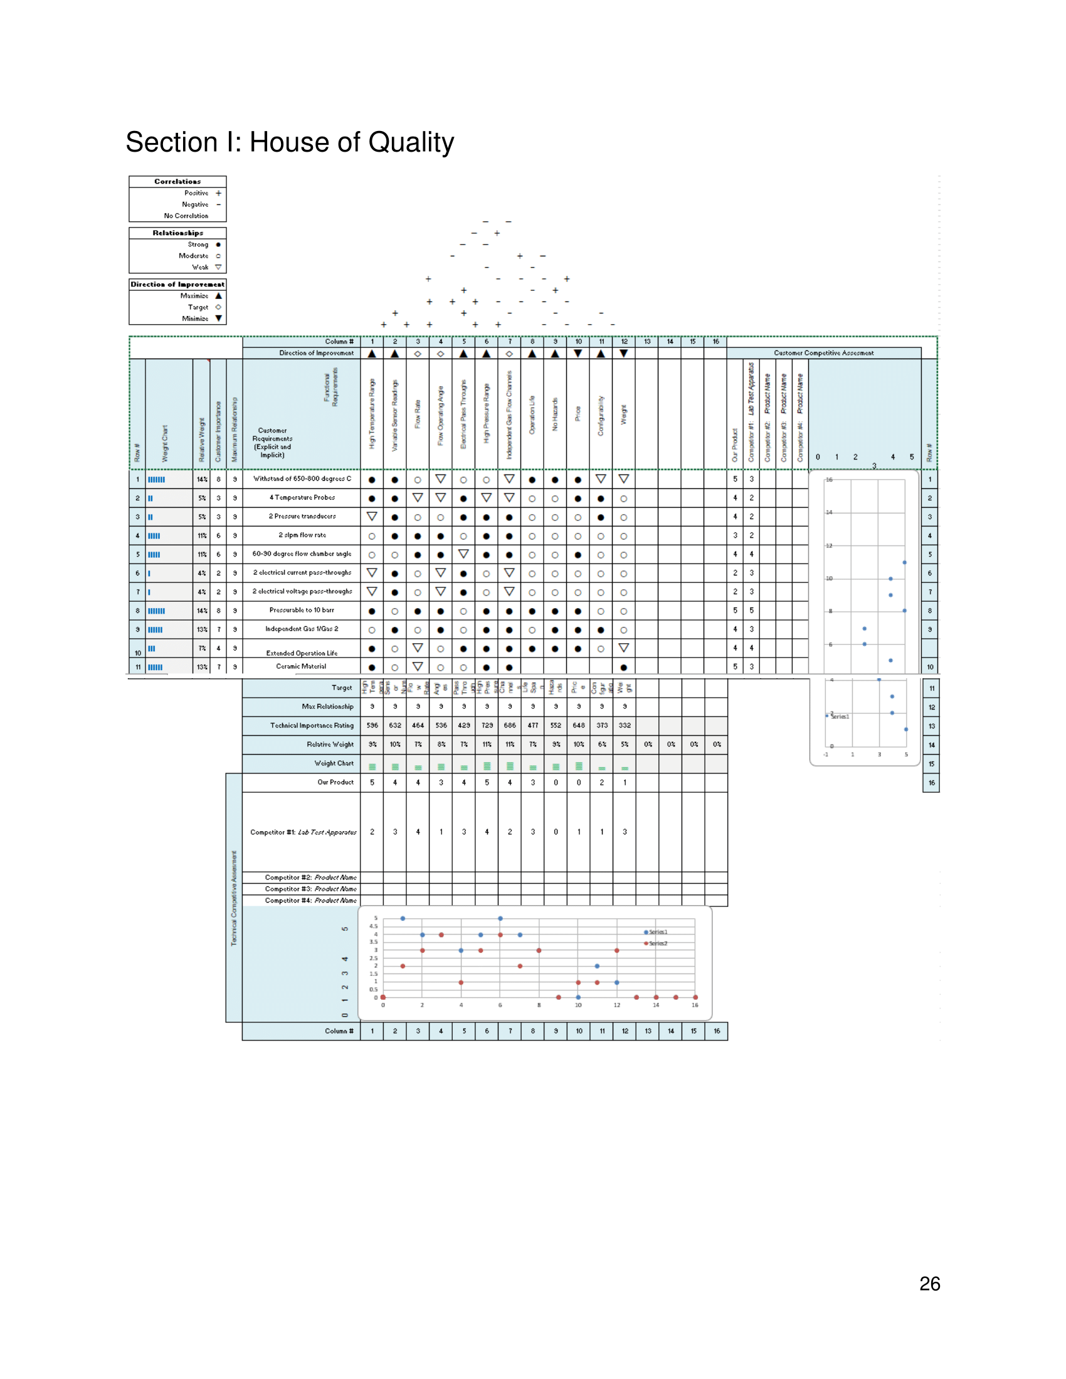
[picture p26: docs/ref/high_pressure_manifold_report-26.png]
report-26


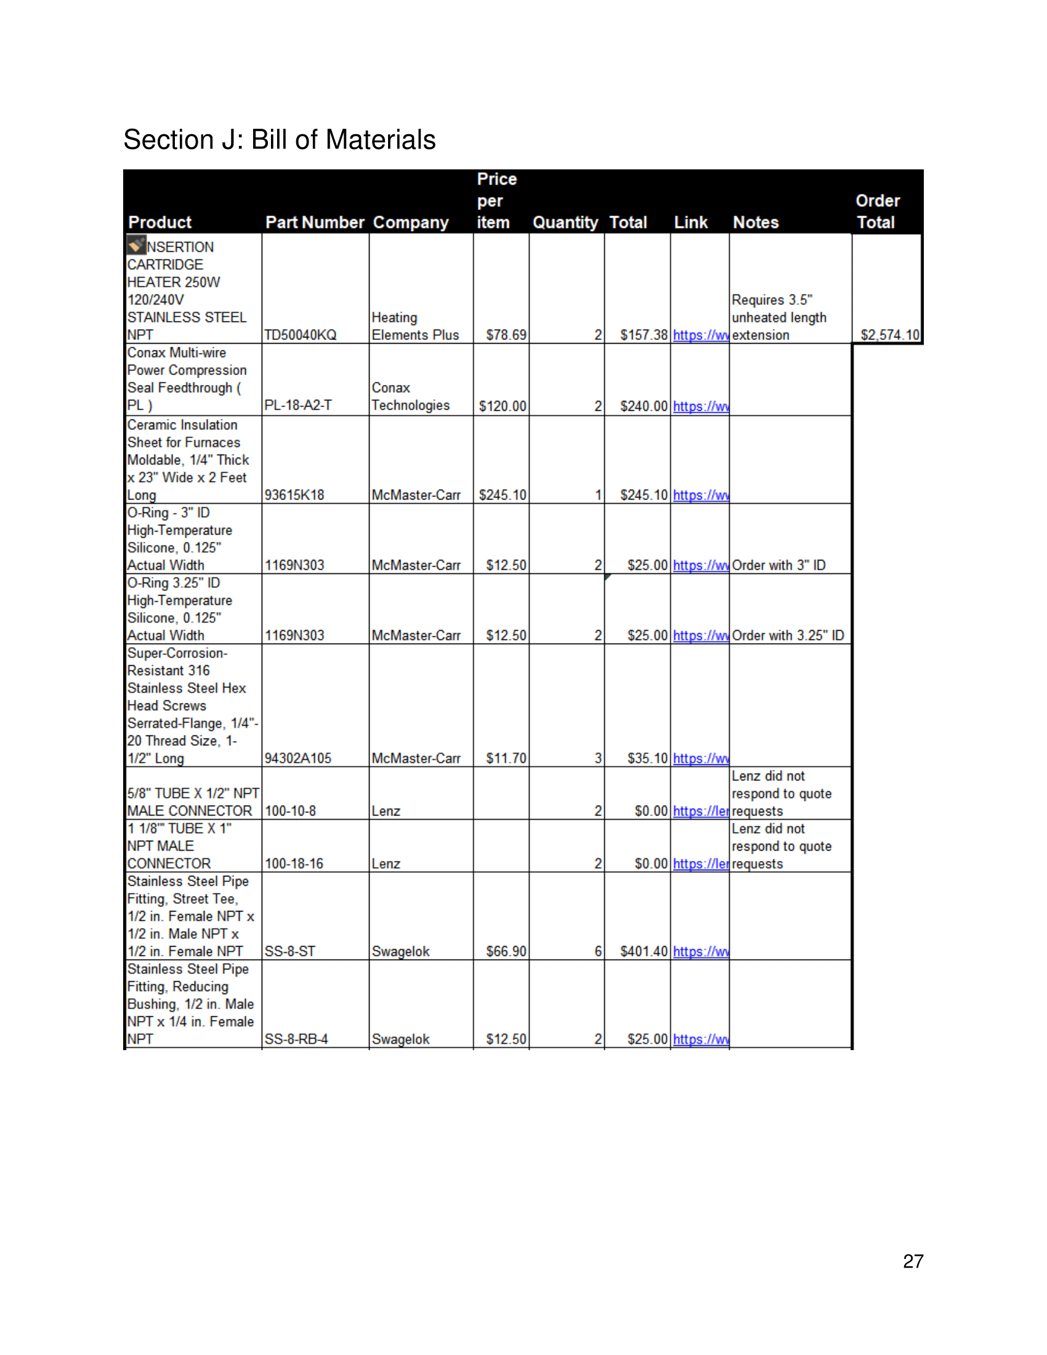
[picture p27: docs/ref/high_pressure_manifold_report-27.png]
report-27


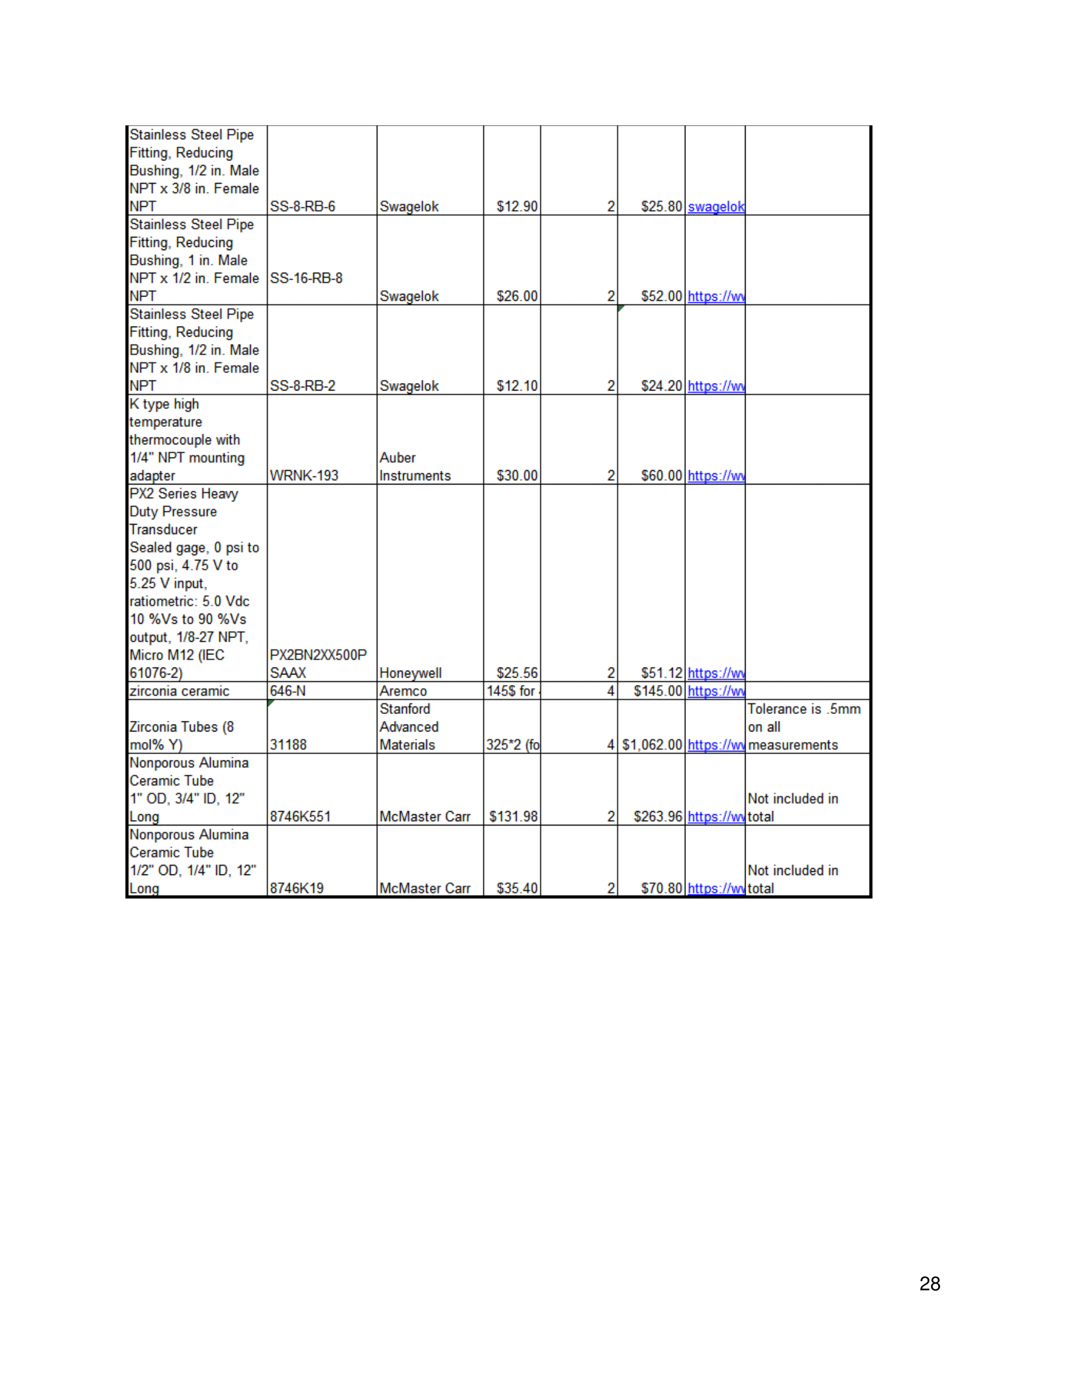
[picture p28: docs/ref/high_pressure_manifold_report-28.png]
report-28


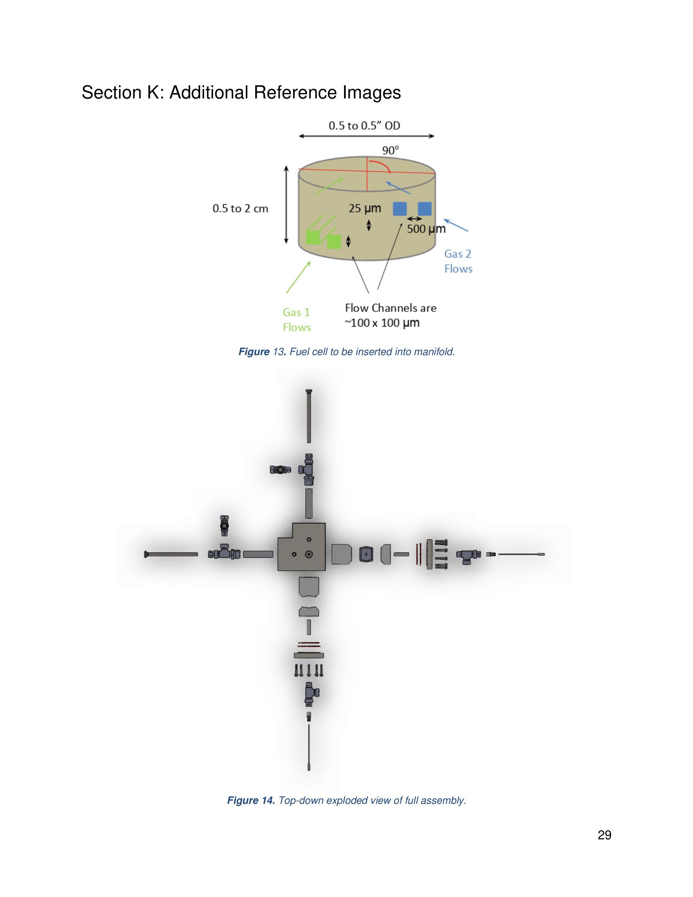
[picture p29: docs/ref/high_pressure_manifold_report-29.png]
report-29


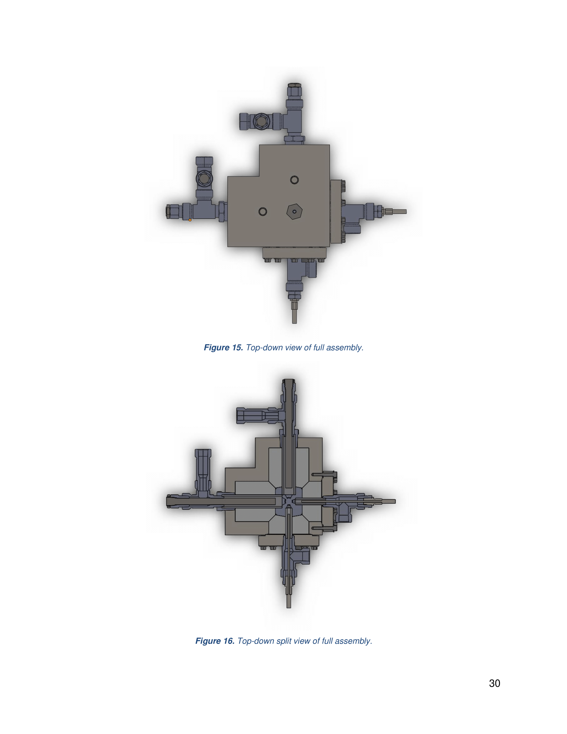
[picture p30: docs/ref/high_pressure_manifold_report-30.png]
report-30


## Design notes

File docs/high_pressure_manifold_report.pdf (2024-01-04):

# High Pressure Manifold

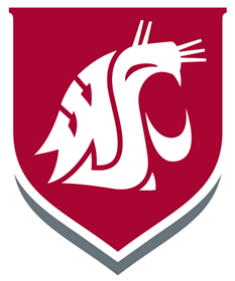
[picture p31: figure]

## 1 GigaWatt Group

Cory Groden, Daelin Malizia, Jonathan Cochran, Justin Brundage, Steven Luick

Dr. Dustin McLarty
Clean Energy Systems Integration Lab

## Table of Contents

Table of Contents | 2
Executive Summary | 3
Introduction | 4
Results/Discussion | 5
Section 1: Manifold Material Selection | 5
Section 2: Manifold Design | 6
Section 3: Manifold Mold | 7
Section 4: Thermo-Fluid Design | 9
Section 5: Instruments | 10
Section 6: Pressure Vessel Design | 11
Section 7: Gas Seal Selection | 13
Next Steps | 16
Appendices | 17
Section A: Casting Mold Assembly Procedure | 17
Section B: Pressure Vessel Assembly Procedure | 18
Section C: Initial Manifold Concepts | 20
Section D: Thermal Design Calculations | 21
Section E: Thermal Flow Rate Calculations | 22
Section F: Insulation Forming Technique | 23
Section G: Bolt Mounting Calculations | 23
Section H: Manufactured Parts | 24
Pressure Vessel | 24
Flange | 25
Section I: House of Quality | 26
Section J: Bill of Materials | 27
Section K: Additional Reference Images | 29

## Executive Summary

Dr. Dustin McLarty and the Clean Energy Lab Site (CESI) group at Washington State University have created a miniature battery cell made of VYSZion, a solid oxide material. Currently, the sole testing method for the fuel cell is a large pressurized chamber, which is far larger than required for testing and the end application of the battery. To optimize a testing device and display realistic operating conditions for the fuel cell, our team at Washington State University was recruited to design a high-pressure manifold. This manifold must be operable in temperatures of 650-800°C and pressures up to 10 bar. It must also have two inlets and outlets, one each for gas and air, and allow for insertion of temperature probes, pressure sensors, and electrical wires.

At the beginning of this project, we were tasked with creating a manifold that would house the fuel cell within the center of the structure. We also needed to create the pressure vessel that the manifold would sit in while the fuel cell was tested. During the second half of the semester, due to circumstances outside of the group's control, we were restricted in what we could do. This changed the objective of the project from creating and testing the manifold and pressure vessel to creating the plans and designs them. Thermal fluid studies to determine tube length and cartridge heater selection have been performed. A castable zirconia for the manifold has been selected based on highest chance of success. The manifold, its mold, the pressure vessel, and flanges have been designed and drawings provided to the client. All fittings and instruments connected to the pressure vessel have been modeled. A production and assembly procedure for both the manifold and pressure vessel has also been specified. Final submission to the machine shop for the pressure vessel and parts ordering will need to be completed by Dr. McLarty and his lab group. Following this, assembly of the manifold and pressure vessel according to the provided procedure will need to be performed. Final testing and analysis of the experiment can be achieved after the assembly is completed. Alterations to any parts in this project’s design can be made if desired results from testing are not met in the future.

## Introduction

The 1 GigaWatt group was tasked with delivering a high-pressure manifold to Professor Dustin McLarty and the CESI laboratory group. The lab group is testing VYSZion, a novel material for fuel cells, in an experiment to determine if VYSZion fuel cells can be used to replace conventional batteries for high powered systems. The design we were tasked with creating includes a ceramic manifold able to house one of these fuel cells for testing and a surrounding pressure vessel to contain the experiment. This design is to be used for testing a single cell at a time for the CESI lab group.

Our primary goals for this project are to design a manifold that can house a fuel cell and a pressure vessel capable of delivering gas to the manifold. The manifold is made of a zirconia ceramic and can withstand high temperatures. The pressure vessel is made of stainless steel and holds ceramic tubes that deliver heated and pressurized gas to the manifold. The vessel can withstand at least 10 bar of pressure. The manifold allows for electrical current from the fuel cell to be measured and the pressure vessel contains various sensors to record pressure and temperature during experimentation.

Professor McLarty’s current lab equipment contains a furnace that is used for other experiments that we were able to base measurements on, such as gas line connections. We were also given requirements that we needed to include in our design parameters.

- The gas range would be between 650 to 800 degrees Celsius
- 4 temperature probes needed: two at inlet, two at outlet
- 2 pressure transducers
- 2 electrical pass-throughs for collecting current
- 2 electrical pass-throughs for collecting voltage
- Gas pressure can reach up to 10 bar
- Gas lines remain independent of one another

Based on these requirements, a zirconia ceramic cast was designed to cast the manifold. The pressure vessel design was created based on results of a thermo-fluid study of the gas that flowed through the experiment. The final product was determined to be a stainless-steel pressure vessel with zirconia gas tubes that connected to the casted manifold, which held the fuel cell.

## Results/Discussion

## Section 1: Manifold Material Selection

For the manifold material, a ceramic is needed due to a high working temperature. Based on initial recommendations of the lab group, cubic zirconia was originally considered. However, cubic zirconia is expensive and has a non-castability, so a regular zirconia was selected.

Zirconia has three phases: a monoclinic structure (<1150C), tetragonal structure (1150-2100C), and a cubic phase (>2100C). The high temperature phases can be stabilized by the addition of Yttrium oxide. Some cubic zirconia will convert back to monoclinic zirconia over time due to uneven heating. This causes volume changes in the manifold which could lead to cracking and failure.

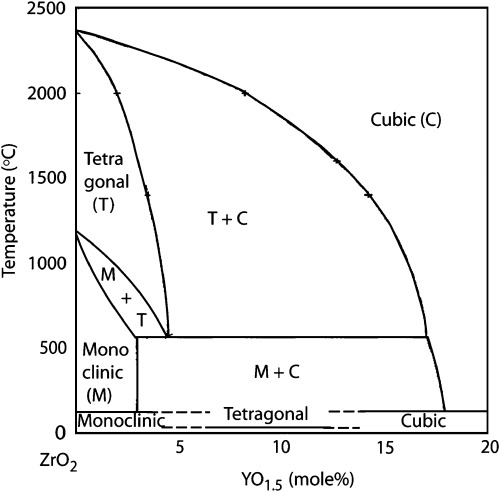
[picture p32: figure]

For the tubes, however, using cubic zirconia tubes was proposed. A zirconia tube will adhere better to stainless steel and the zirconia manifold. In addition, high temperature gases will be passed through the tubes for an indefinite amount of time. The composition of the selected tubes is 8 mol % Yttria stabilized Zirconia. This composition, with respect to the phase diagram in Figure 1, and how it is processed, should stabilize the cubic phase at the operating temperature. The tubes are also small enough meaning that heating will be more even, so changes in volume should be negligible. Tubes will be joined to the manifold via the leftover zirconia slurry. The large downside of these YSZ tubes is that they come with a price tag of 1062$. Therefore, alumina tubes were also proposed. These tubes cost between 100-200$, which is a significant decrease. However, alumina will not join with the manifold as well as the YSZ tubes since they are not the same material.

Figure 1. Phase diagram of ZrO2 and YO1.5

Precaution will need to be considered for the processing of the manifold. It is most likely that any failure in the entire part will be due to processing defects in the manifold or tubes. Ceramics are notorious for cracking during processing or post processing and can undergo fatigue cracking or failure over time. So, for post processing of the manifold, the voids, moisture, and binding agents will need to be removed slowly to avoid cracking. Typically, increasing the post processing time will decrease the number of micro cracks formed. Cracks and micro cracks due to processing will be a big problem in the final manifold part, as due to the high manufacturing temperature, it will be easier for those cracks to propagate and for dislocations to move.

The procedure is specified in Appendices Section A: Casting Mold Assembly Procedure.

## Section 2: Manifold Design

A manifold was designed that will direct gas at and house a 1 cm diameter VYSZion fuel cell. There needed to be inlets and outlets at opposite sides with an angled approach towards the fuel cell, preferably with a 60-degree cut and 30 degree spacing.

Two different iterations of the basic design of the manifold were thought of initially, one being cube-like and the other being cylindrical. Provided in Appendices Section C: Initial Manifold Concepts is a basic sketch and understanding at the time of the manifold model idea conception. This can be compared to the final design seen in Figure 2.

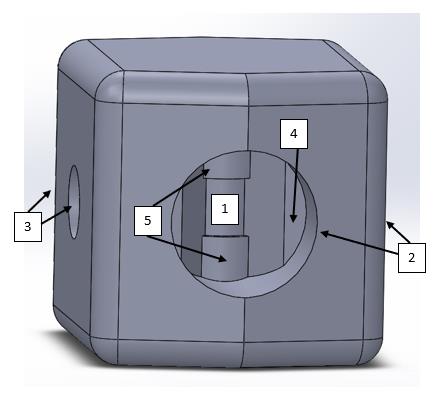
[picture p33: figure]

Figure 2. Completed model of the manifold.

The following list indicates what is present in the model:

1. Fuel cell in the center of the manifold.
2. Large tube entrances for the hot air and gas to enter (front and right sides), where it will push against the fuel cell.
3. Small tube entrances for the hot air and gas to exit (left and back sides).
4. Flat wall for the tubes to press up against. This is on all sides in the tube entrances and exits.
5. Fuel cell holder, where the fuel cell will be placed in between and held there. Wires will enter and exit on both sides of the fuel cell and should be protected by these holders.

Several of the major changes involved changing the basic shape from a cube to a cubic hexagon. The main reasoning behind that is so that there is a specific way the manifold would be placed inside the pressure vessel. The dimensions of the manifold needed to be big enough to provide enough insulation around the piping. The base measures 2x2x2 inches, with a 0.18-inch edge on the corned side. There are two different holes for the piping to fit in, with the large pipes measuring 1 inch in diameter and ½ inch for the smaller pipes. The edges of the manifold were softened as to provide better support for the overall structure. Initially, the manifold had an opening over the top of the fuel cell but was later filled in when more information was made known.

## Section 3: Manifold Mold

With the main structure created, a mold needed to be created to cast the manifold. There was some talk about a 4-wall assembly with a 2-piece outer holder that would hold the walls together, as it would hopefully save on filler material that would be responsible for holding up the negative tubing in the mold. But it was decided initially to stick with a 2-piece set, as the mold will be melted off of the manifold after it is solidified, and that if the walls have trouble aligning, it could cause the cast to solidify incorrectly. The 4-wall cast could be tested to create the full cast.

Initially, the cast cut right through the middle of the manifold. However, it was discussed and decided that the piping should all remain on one part, as to provide uniformity in the finished model, and then have a lid that would be used to pour the Zirconia material inside. Two holes can be seen on top of the cover mold. These are where wires that connect to the fuel cell will be pushed through.

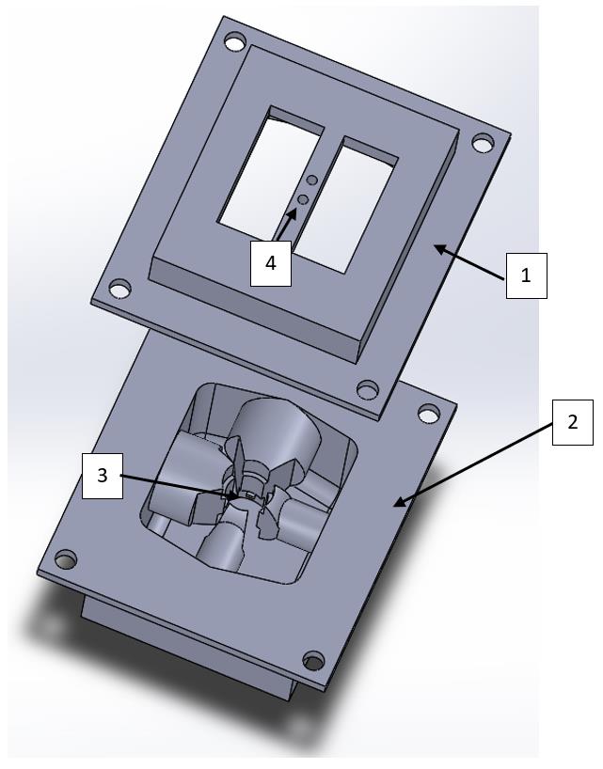
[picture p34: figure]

In Figure 3, the negative mold for the manifold is shown. The following are included within the negative mold:

1. Top plate for the mold, where holes can be used to align and bolt the mold together.
2. Bottom plate for the mold. With the negative areas to create cavities for the piping.
3. Area for the fuel cell to sit. There are notches within this area to help provide some support for when the fuel cell is placed within and the mixture is poured in.
4. Holes on the top of the mold for wires to come out. These should help keep the wires apart while pouring the mixture.

Figure 3. Negative mold for creating the manifold.

While creating the part, the fuel cell puck should be placed within the set area in the center of the cast, resting on the notches that help keep it up while the zirconia is being poured. The wires attached to the fuel cell snake through the holes on the top part. Then the two pieces should be glued and brought together, bolted with ¼ inch bolts in each corner hole. This will help keep the mold aligned and stay in place as the material is poured inside. Once set, the zirconia can be poured into the mold until it reaches the bottom surface of the wire bar.

After it is cast and has finished setting, the mold can then be melted off the finished manifold. If additional wires are needed, a drill can cut a couple of holes at the bottom of the manifold and be attached to the fuel cell if needed.

## Section 4: Thermo-Fluid Design

The pressure vessel was designed based on the thermo-fluid parameters specified in the House of Quality (HOQ). To design an optimized system, a simulation needed to be performed to determine specifications for tube lengths and heating elements.

Using SOLIDWORKS Flow Simulation, the thermo-fluid study was created in these following steps:

1) A zirconia tube was modeled and then surrounded by another tube made of alumina silica for insulation.
Two diameter sizes were made in order to optimize for the best design:
- ¾ in
- 1 in
2) A computational fluid dynamic study was created to find the temperature change within the zirconia tube that the gases will flow through.
3) A cartridge heater was modeled and placed within the zirconia tube for the simulation with variable heat fluxes.
4) The length of the zirconia tube and insulation tubes varied to find a length that will reach the desired temperatures.
5) After the simulation was completed the following specifications were determined:
- Length of the tubes is 4.5 in
- ½ in diameter cartridge heater with 250 W power output
- Tube diameter of ¾ in

We performed calculations to find the temperature on the outer layer of the insulation. In Appendices Section D: Thermal Design Calculations and Section E: Thermal Flow Rate Calculations are the methods used and the results of these calculations.

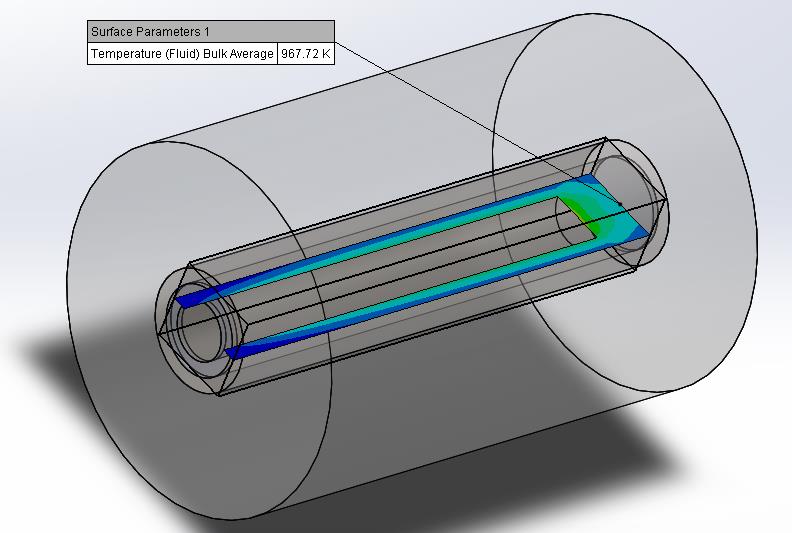
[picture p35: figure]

Figure 4. Thermal fluid study to determine exit temperature.

Since the two gases that will be used in the experiment are similar in composition, we were able to mirror the results of the study and make a symmetric design for the pressure vessel.

The result of the pressure vessel entrance contains:

- Two 4.5 in zirconia tubes with 1 in OD and ¾ in ID
- Two insulation tubes
- Two 250 W cartridge heaters

## Section 5: Instruments

There are three different instruments which will be connected to the pressure vessel and provide feedback from the system:

- Cartridge Heaters
- Pressure Transducers
- Thermocouples

Due to the configuration of the Lenz fitting and required adapters, the cartridge heater must be longer than the previously determined length. The cartridge heaters will be 7.5 in in total length with 3.5 in of unheated length.

The unheated length is the portion that will sit within the fitting, and the portion that will be heated will be the originally determined length needed to heat the gases to desired operating temperatures.

Pressure transducer location changed from being toward the center of the pressure vessel downstream to the unheated portion of gas flow. As such, high temperature tolerance transducers were no longer needed. The new pressure transducers are:

- Heavy Duty Pressure Transducers (Honeywell)
- Can withstand up to 35 bar

Thermocouples were selected based on ability to reach near the center of the cast manifold and NPT threading capability. Being able to read temperatures inside the manifold allows the CESI group to determine if the cartridge heater is heating the gas/air too high and adjust its power output. In the future they plan to add a PID feedback system to automatically adjust power output so gas/air into the manifold is always in the desired range.

## Section 6: Pressure Vessel Design

With the specified temperatures and pressures into the casted manifold being much higher than ambient levels, a pressure vessel is required to maintain an ideal environment for testing. The following are key specifications the vessel was designed around:

- Inlet length is long enough for cartridge heaters to heat incoming air/gas to 650°C to 800°C.
- Bores are large enough that insulation, zirconia tubes, and manifold can be inserted.
- Each of the given requirements for sensors, electrical pass-throughs, and environmental conditions are met.

With these considerations in mind, an initial design for the pressure vessel was created.

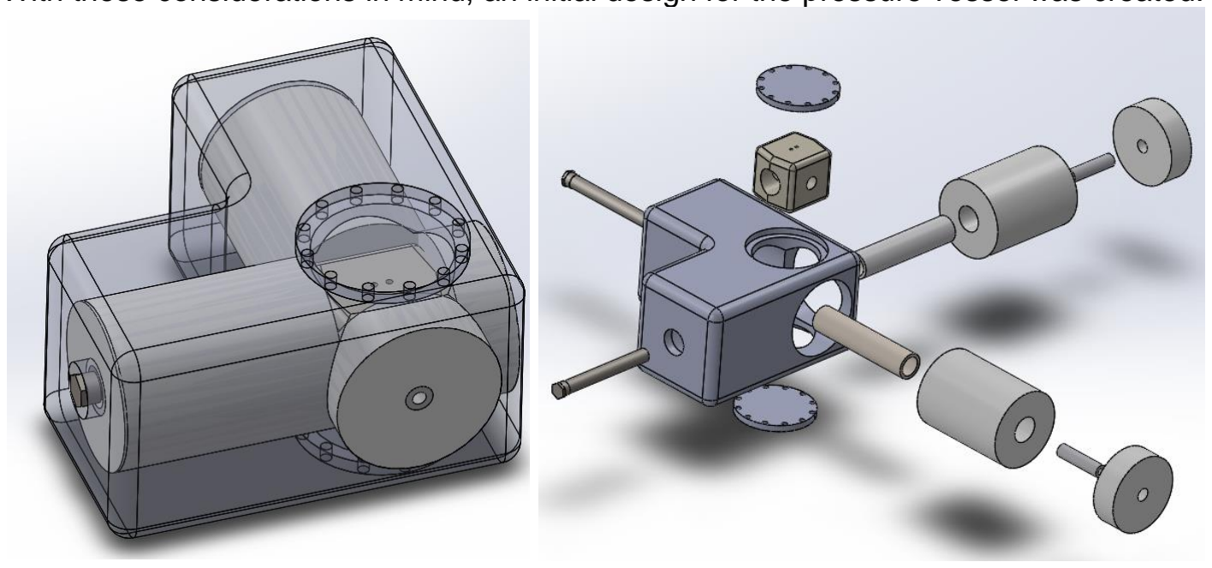
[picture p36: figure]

Figure 5. Initial pressure vessel design with exploded view.

The design in Figure 5 contained some parts used in the overall design but had some key flaws:

- The top flange was not necessary, electrical passthroughs could thread into the vessel itself.
- No attachments for how the cartridge heaters or ceramic tubes would connect to the vessel had been determined.
- Sealing for the large bore holes had not been determined.
- The thickness of the vessel is too small if a flange is to be connected to it.

After multiple design reviews and adjustments to the design, a refined version was modeled.

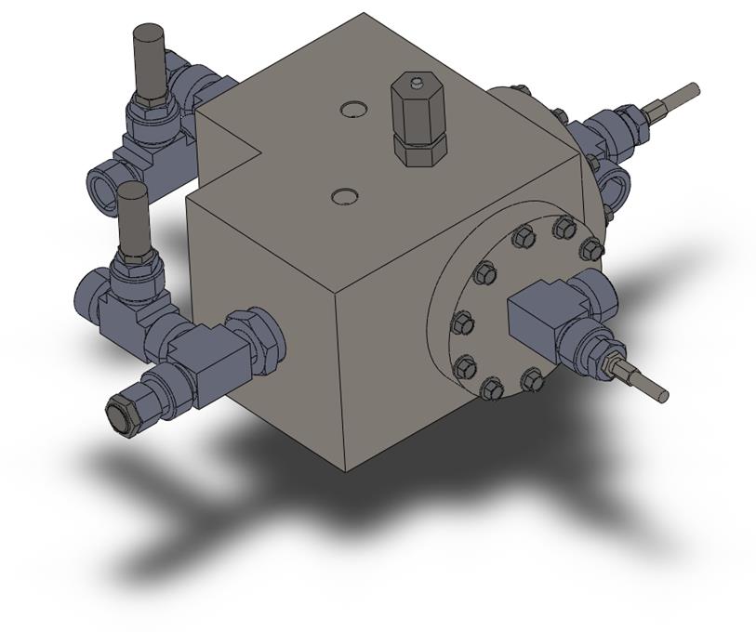
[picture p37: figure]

Figure 6. Final pressure vessel design.

This version included all attachments and instruments that would be connected to the pressure vessel. Design changes that were made from the original version:

- The ¼” NPT threaded holes on the top were changed from being for pressure transducers to being there as openings to pressurize the vessel. This change was made since the pressure transducers could be moved to the fitting configuration at the gas inlets.
- Size of the vessel was adjusted from 4” thick to 5” thick so the flange parts could fit around the vessel
- Insertion holes were chamfered so insertion of sensors and probes is a self-locating process.

- Gasket size was reduced to decrease surface area so a higher pressure can be reached to ensure a better seal.
- Graphite gasket was changed to Silicone O-rings. This change was made to increase sealing functionality as silicone O-rings are readily available at a smaller diameter
- Second O-ring added as backup in the event one either cannot withstand the temperature or pressure it is exposed to.
- Flange design was changed from flat face (FF) to raised face (RF). This creates a small gap between flange and the pressure vessel, so the flange is only touching the gasket, creating a tighter seal.

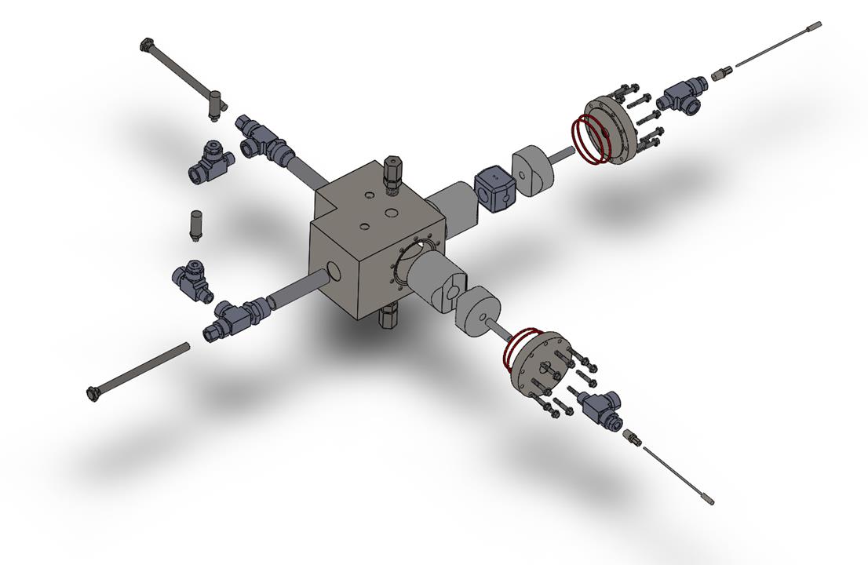
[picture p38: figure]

Figure 7. Exploded view of final pressure vessel design.

## Section 7: Gas Seal Selection

Once tube diameters were decided to insulate the high temperatures, the task of finding a way to route the gas, seal the system, while properly heating the gas arose. This becomes challenging due to having to think outside of the box when using manufacturer parts.

Initially, a Swagelok system was designed to connect a linear path from gas to manifold. The four part system, consisting of a NPT body, NPT to VCR converter, VCR tube butt weld, and a VCR coupling, with the cartridge heater in the tube weld, supported by a metal support ring designed by me. This was rejected by our client due to previous difficulties with Swagelok sealing. Instead, a Lenz seal configuration at the pressure manifold interface was proposed.
The Lenz seal was selected because the pressure manifold has a controlled hole size. A seal was selected based off the entrance hole, and an NPT reducer was selected to go down to the size of the cartridge heater. A Swagelok tee fitting was selected to house the cartridge heater on the straight end. This would allow for the gas to be diverted in and around the heater, with the NPT fitting of the heater to be sturdily sealed, instead of on its own fitting. Figure 8 shows this configuration.

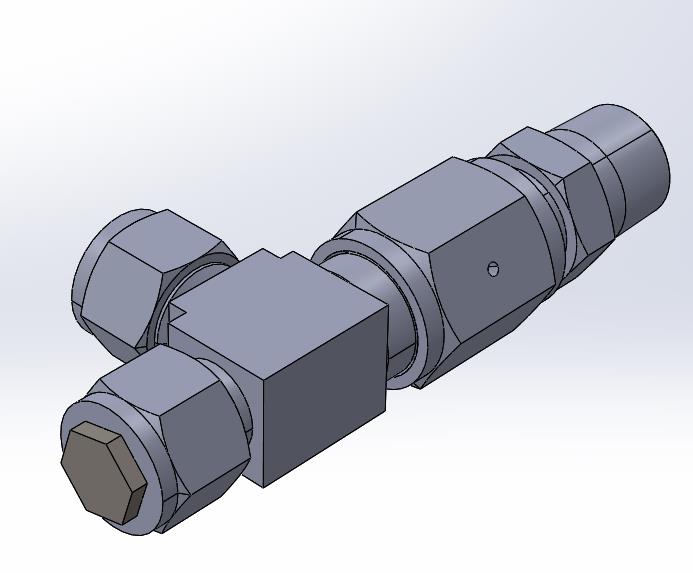
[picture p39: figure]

After a design meeting, we found we needed to create a similar but smaller connection seal for the exit gas/air. In this configuration, the tee would have had to be bored out to allow for the heater to sit in the tee fitting. If this happened though, the tee would break because there was not enough clearance in the piece. A new configuration was then created.

This configuration started with the Lenz seal again. The entrance needed a slightly larger seal than the initial one for the exit. A large enough tee fitting was then chosen, so the cartridge heater could fit. It was also important to decide what kind of connector, male or female, and what size was chosen because not every configuration of these two exists. A reducer was used to connect the Lenz seal to the tee fitting, and a different reducer was chosen to connect the cartridge heater to the tee. The tee fitting in this new configuration will need to be slightly bored out. Figure 9 shows the entrance and Figure 10 the exit. The entrance seal has one extra reducer than the exit seal.

Figure 8. Initial seal configuration.

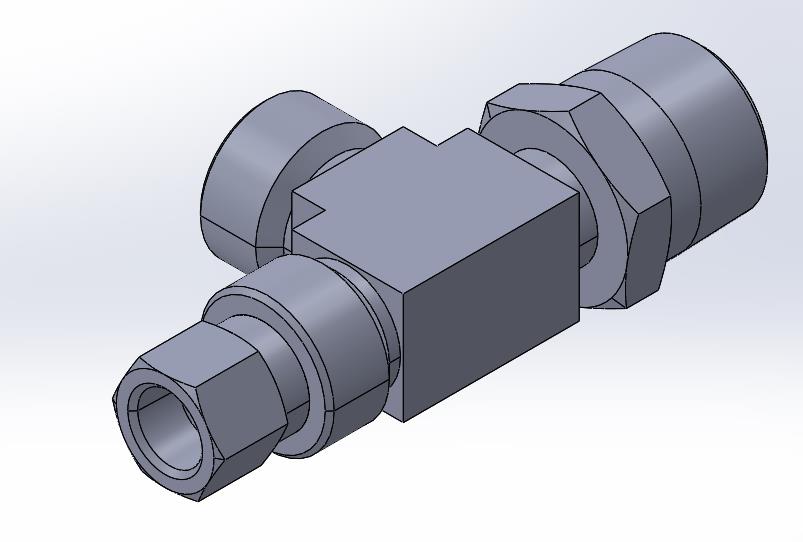
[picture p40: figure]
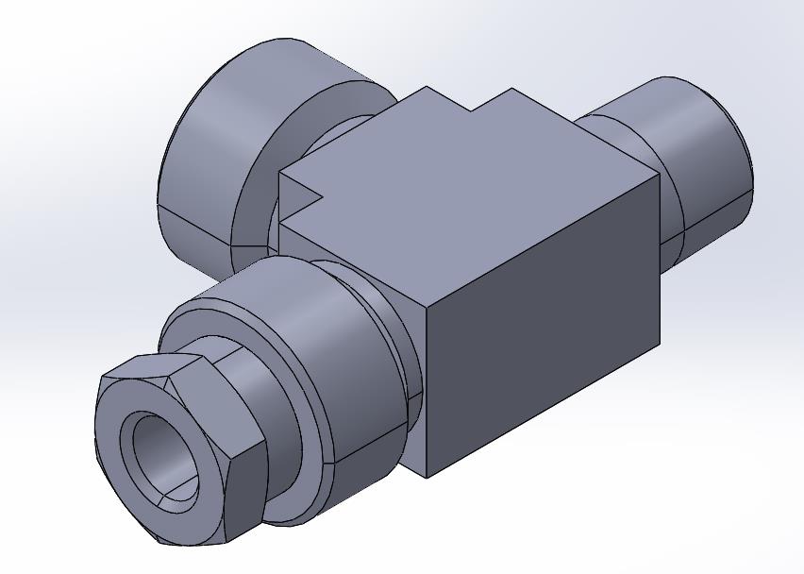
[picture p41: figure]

With this configuration, the cartridge heater's unheated length was extended by a few inches. This ensures the gas will retain its heat in the ceramic tubes, and not get too hot in the metal fittings.

Figure 9. Final entrance seal configuration.

Figure 10. Final exit seal configuration.

## Next Steps

Using various materials, manufacturing techniques, and connectors our team was able to come up with a plan for creating a pressure vessel and manifold for a fuel cell that operates at high temperatures. Various calculation and material property checks were performed to ensure the success of the prototype. Additionally, the prototype meets all the high end of all requirements mentioned in the introduction.

The next steps that should be taken in this project is submission of designs to the machine shop when the quote for machining costs is received. Parts also need to be ordered. Assembly according to the procedure in Appendices Section A: Casting Mold Assembly Procedure and Section B: Pressure Vessel Assembly Procedure need to be completed and then testing can move forward. Additional changes that could be made to the project are optimizing the cost of the prototype and pressure vessel and adding safety features.

A safety feature that would be useful is a ceramic pressure sensor (needs to be ceramic because of the high temperatures). This would detect any unusual shift in pressure, whether too low or too high, and shut down the system to prevent catastrophic failure of the manifold and/or the pressure vessel. Although this is already a pressure sensor installed, this one would automatically shut the system down instead of needing someone to manually do it.

To reduce costs, it is possible that alumina tubes can be used instead of zirconia tubes to reduce the overall cost. Another change that can be made is to buy pre-manufactured a steel vessel with six inlets instead of machining one ourselves. This would significantly lower the machining costs. However, the flanges would still need to be added, so it would make assembly slightly more difficult. Design changes can also be made to reduce overall cost as well, as making it easier to machine will lower the machining costs.

## Appendices

## Section A: Casting Mold Assembly Procedure

Phase 1: Slurry Preparation
1. Mix the zirconia powder and water at a 100:12-14 ratio. A hydrophobic liquid can also be used in place of water at the same ratio, but moisture likely won’t be a problem at these high temperatures
2. Mix thoroughly to get an even composition and start to eliminate air bubbles using an ultrasonicator and/or a vacuum chamber.
3. For the vacuum chamber, wait until it stops bubbling then remove the casting slurry.

Phase 2: Molding
1. 3D Print the two assembly pieces
2. Place Fuel cell in designated area in the center of the cast [3]
3. Apply paste to the faces that will meet together on both parts (bottom of [1], top of [2])
4. Thread the fuel cell wires through the top holes on the top cast part [4].
a. Optional: drill two holes at the bottom of [2] if needed to thread the bottom wires
b. Use some sort of stopper at the bottom to prevent leakage
5. Apply ¼ in bolts to the holes in [1] and [2] to align the cast and press together
6. Apply clamps to the cast as paste dries
7. Once set, pour the cast mixture into the mold until it fills up to the bottom of the wire beam
8. Once the mixture is set, melt off the printed mold to expose the finished manifold

Phase 3: Post Processing/Curing
1. Air dry the part overnight. The manual says 8 hours but should be extended.
2. Bake for 4 hours at 200 degrees Fahrenheit. For extra cautionary measures, heat up the furnace or oven slowly to ensure no cracks will form.
3. Cure at 250 degrees Fahrenheit for 3 hours, heating and cooling the furnace slowly.
4. (Alternate) If using the Hydrophobic liquid binder, cure at 450 degrees Fahrenheit for 1 hour instead of step 3. Use extreme caution in heating and cooling the part

For reference, please see https://www.aremco.com/wp-content/uploads/2015/08/A0_Catalog_15.pdf, (https://www.aremco.com/wp-content/uploads/2015/08/A0_Catalog_15.pdf) page 16

## Section B: Pressure Vessel Assembly Procedure

1. Prepare ceramic insulation by wrapping around 1” OD zirconia tubes until insulation OD is 3”. Insulation should be 3” long.
2. Cut away excess insulation so it fits flush within pressure vessel and flush against respective wall of the manifold.
3. Repeat steps 1-2 for 0.5” OD zirconia tubes. Insulation should be 1.4375” long.
4. Through the large opening insert ceramic insulation for 1” OD tubes until flush with the opposite wall. Repeat for other side.
5. Place a 1” OD zirconia tube through insulation until at least ¼” length is exposed on the other side.
6. Apply ceramic paste to outside of both zirconia tubes at manifold connection and inside of manifold where connection will be made.
7. Attach free zirconia tube into manifold until it hits inside stopper.
8. Insert manifold into pressure vessel such that the attached zirconia tube goes through the empty ceramic insulation until it is exposed on other side of vessel.
9. Ensure the other 1” hole for the manifold is aligned with the previously inserted zirconia tube.
10.Push zirconia tube into manifold until it hits inside stopper and ensure connection is sealed.
11.Feed electronic wires through top and bottom holes of pressure vessel. 12.Place excess ceramic insulation to openings above and below the manifold to secure it in place.
13.Feed wire into electrical passthroughs.
14.Place the electrical passthroughs on the top and bottom of the pressure vessel and secure into place.
15.Screw 1” NPT Lenz fitting onto one of the zirconia tubes exposed end. Do not tighten fully.
16.Attach 1” to ½” NPT reducing bushing to long end of a Swagelok Tee adapter that will attach to the Lenz fitting.
17.Add ½” to 3/8” to opposite side of Tee adapter.
18.Attach Cartridge heater to 3/8” bushing so it goes through the Tee adapter. 19.Screw Swagelok Tee adapter onto Lenz fitting attached to pressure vessel. 20.Attach a second Swagelok Tee adapter perpendicularly onto the middle of the Tee adapter in the current assembly.
21.Add a ½” to 1/8” reducing bushing to the middle of the second Tee adapter. 22.Place the pressure transducer onto 1/8” bushing and secure.
23.Attach exposed opening of the second Tee adapter to the air/gas supply. 24.Ensure all connections are secure.
25.Repeat steps 15-24 for second zirconia tube.
26.Repeat step 6 for 0.5” OD zirconia tubes.
27.Insert 0.5” OD zirconia tube with insulation around it into opening until flush with manifold.
28.Repeat step 10.
29.Place the two silicon O-rings on the outside of the pressure vessel around the large opening.

30.Place the flange over the O-rings and secure onto pressure vessel using the ¼”-20 screws and the respective holes.
31.Add the 0.5” NPT Lenz fitting into the center of the flange on the second side and secure.
32.Add Swagelok Tee adapter to Lenz fitting.
33.Place the ½” to ¼” reducing bushing to long end of Tee adapter and secure. 34.Place the thermocouple into the first side and reducer and secure. 35.Attach exposed opening of the Tee adapter to the air/gas outlet.
36.Repeat step 24.
37.Repeat steps 26-36 for the second 0.5” OD zirconia tube.

## Section C: Initial Manifold Concepts

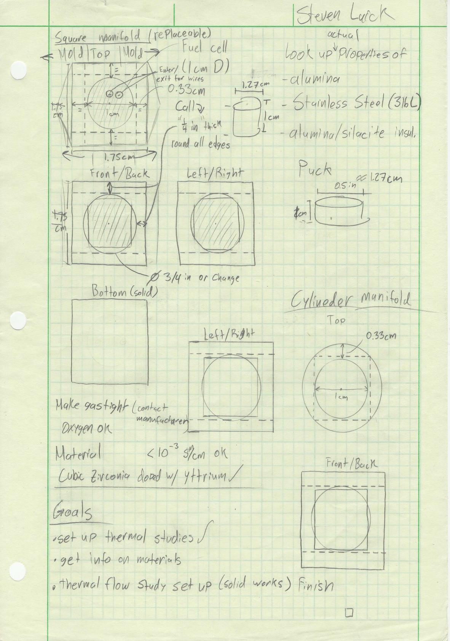
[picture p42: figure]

## Section D: Thermal Design Calculations

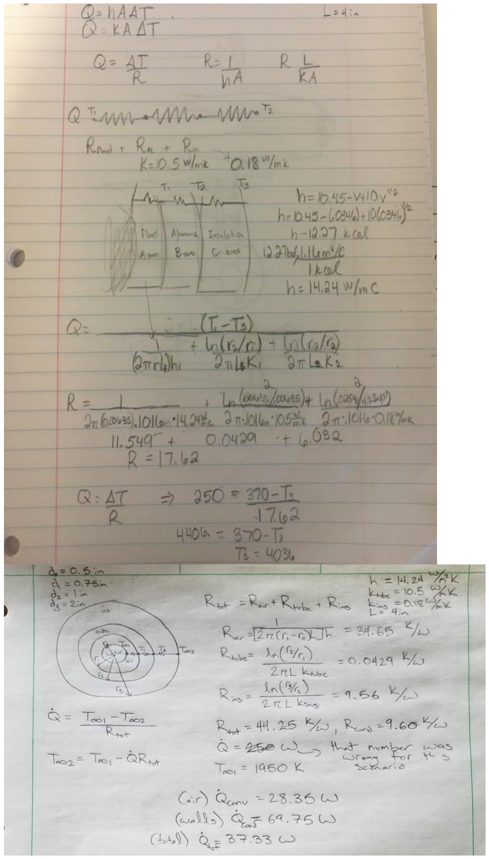
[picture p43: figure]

## Section E: Thermal Flow Rate Calculations

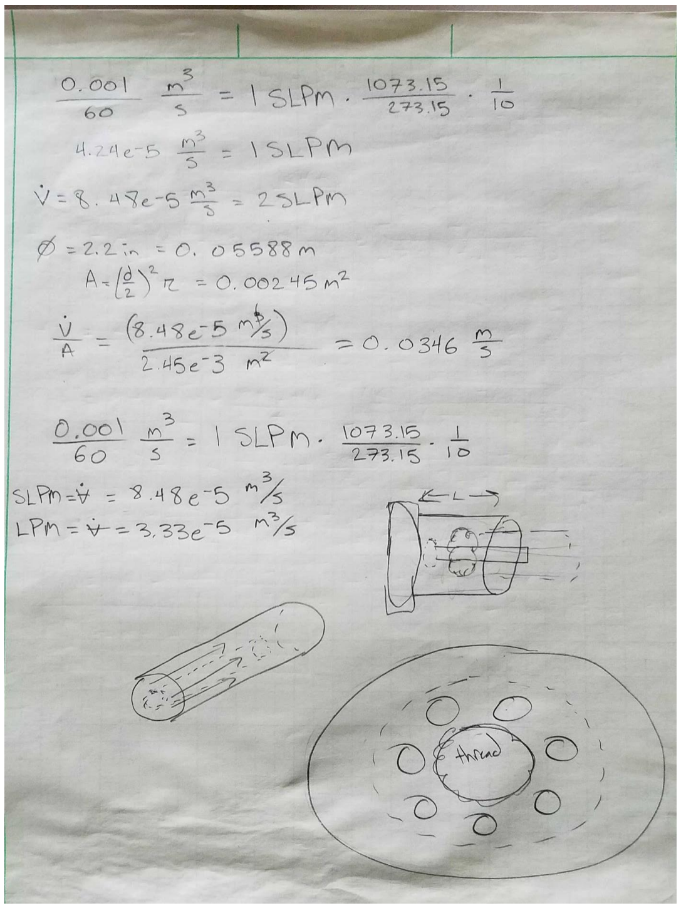
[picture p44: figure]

## Section F: Insulation Forming Technique

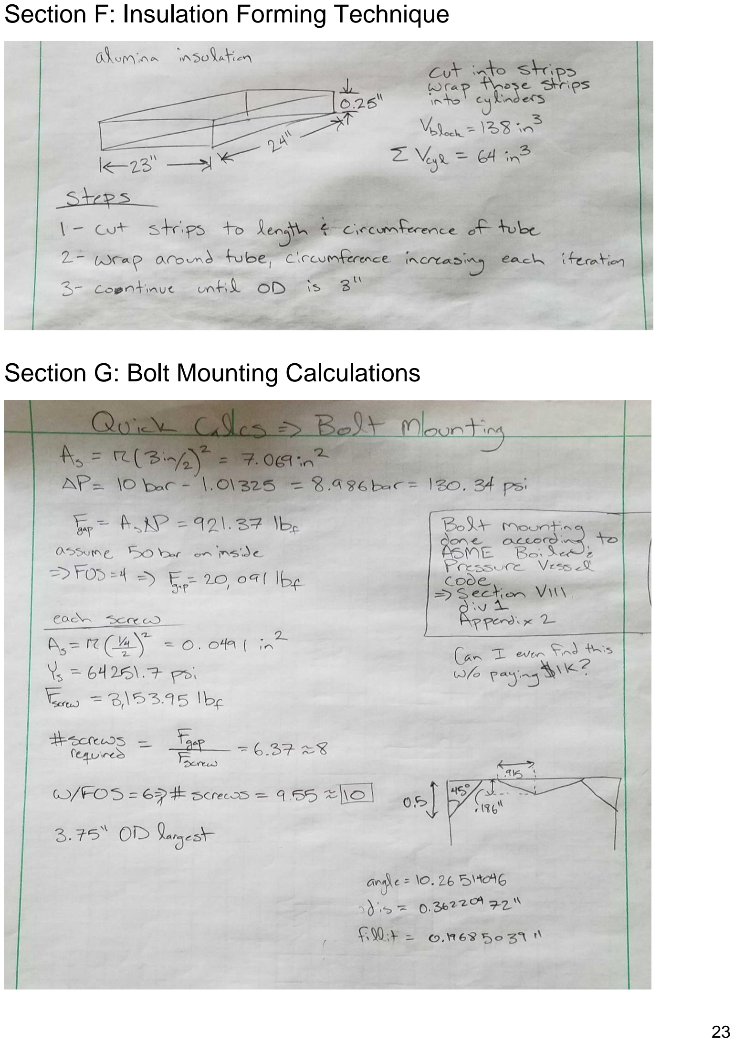
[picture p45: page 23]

## Section G: Bolt Mounting Calculations

## Section H: Manufactured Parts

Pressure Vessel

The pressure vessel is to be machined from a 7.5 in x 7.5 in x 5 in 316 stainless steel block. The specifications for this are based on the final pressure vessel design from Section 6: Pressure Vessel Design. Machining for this has been discussed with the machine shop at WSU but a quote has not yet been obtained from them.

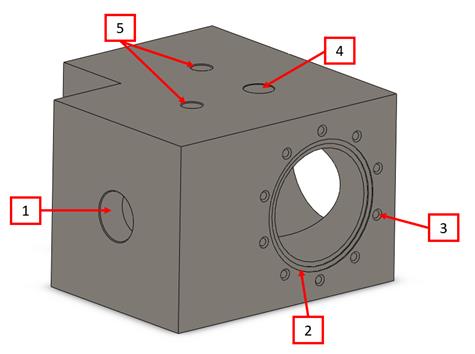
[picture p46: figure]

Connection points onto the exterior of the pressure vessel, numbered in Figure 11, are as designated:

1. 1” NPT threaded hole for Lenz fitting attachment for gas/air inlet that goes in 0.75”. Cartridge heater with internal thermocouple is inserted at this point.
2. Flange connection with double O-ring seal. Both O-rings are 1/32nd” thick and the outer O-ring is a 3.5” diameter while the inner O-ring is a 3.25” diameter.
3. ¼-20 threaded holes are on a 4” diameter ring around the large holes and are 0.75” deep.
4. One ½” NPT threaded hole on top and bottom of pressure vessel where electrical pass-through will sit.
5. Two ¼” NPT threaded holes for insertion of CESI group’s fitting to pressurize the vessel itself. These are located 2.5” from the face of the inlet port.
6. Main bores are 6.5” deep and 3” in diameter.
7. Inlet and outlet sides in 1-3 are mirrored on the other side of the vessel.

Figure 11. Final pressure vessel design.

Flange

A flange is required to seal the pressure vessel after all parts are inserted. It also allows for outlet air/gas configurations to be connected to the manifold. This will also be machined from 316 stainless steel.

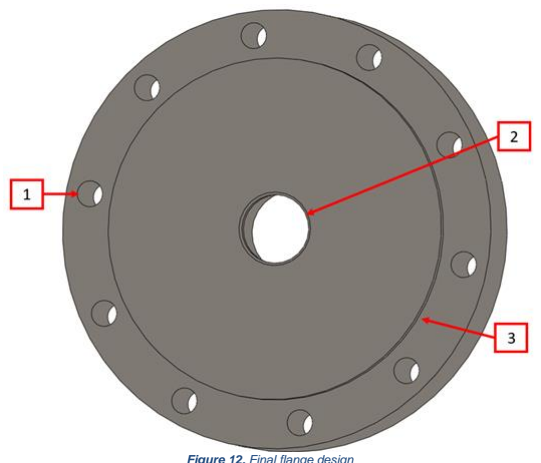
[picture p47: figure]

Connection points onto the flange, numbered in Figure 12, are as designated:

1. ¼-20 Clearance hole; passes through to other side of flange.
2. ½” NPT Lenz fitting attachment for gas/air outlet. A thermocouple is inserted through this connection.
3. 3/32” raised face to compress 1/32” diameter O-ring and create 1/16” gap between flange exterior and pressure vessel.

Figure 12. Final flange design

## Section I: House of Quality

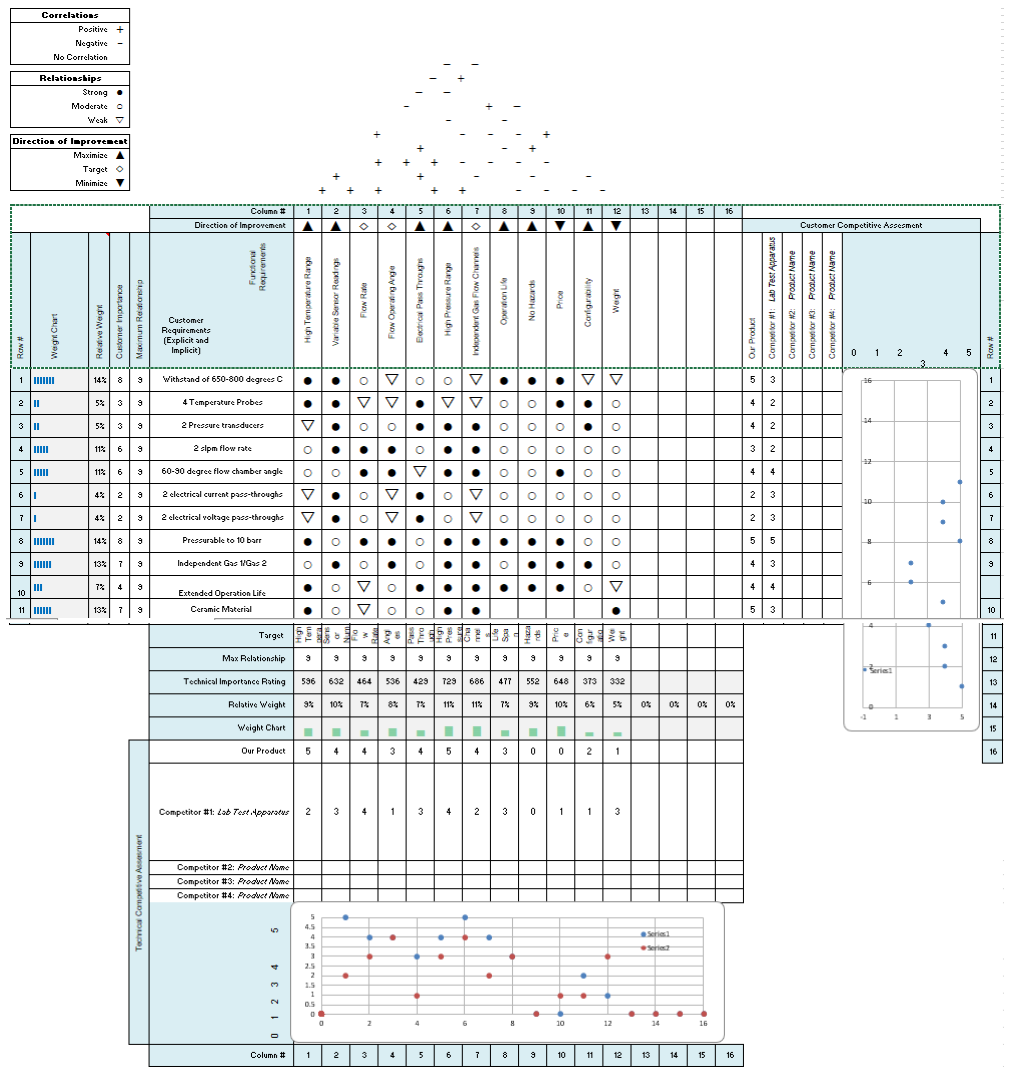
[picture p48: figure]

## Section J: Bill of Materials

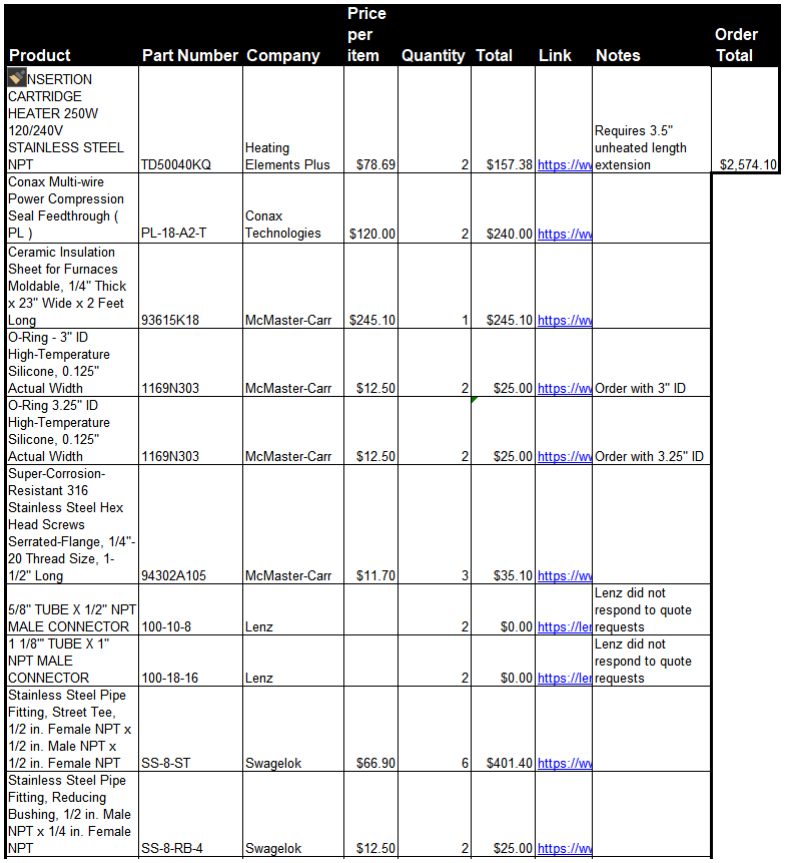
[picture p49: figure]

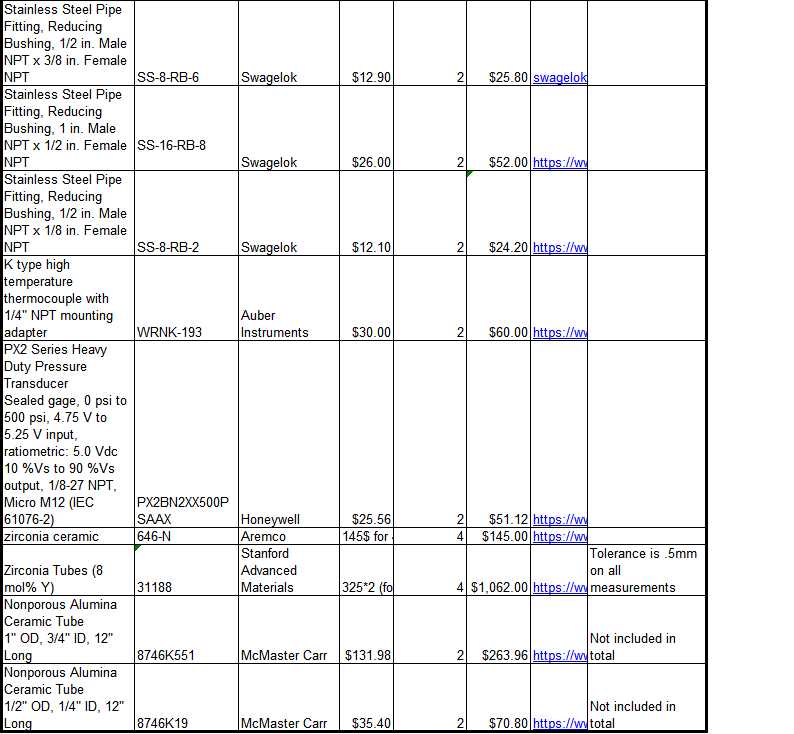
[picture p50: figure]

## Section K: Additional Reference Images

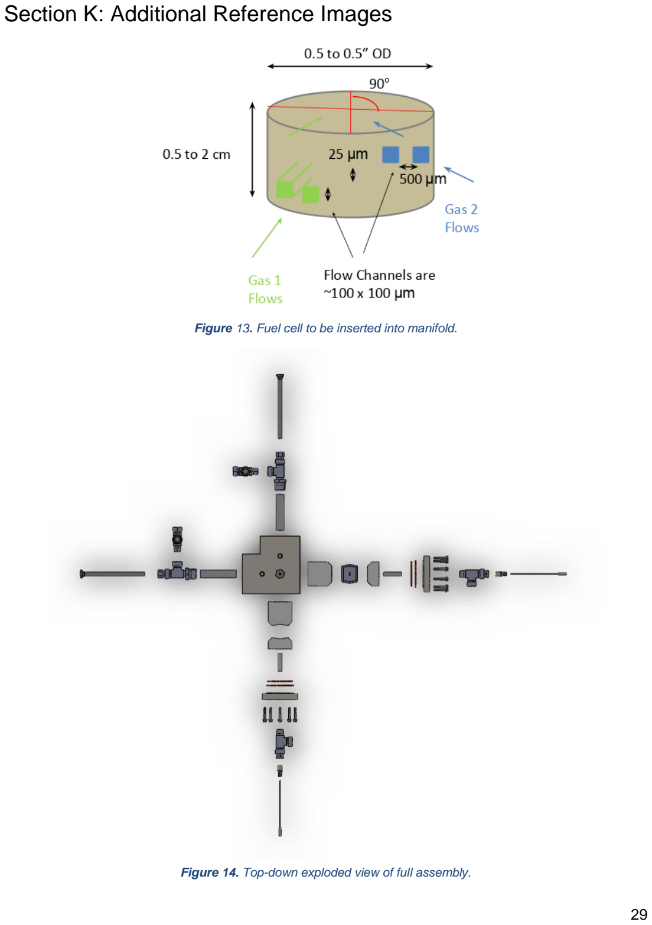
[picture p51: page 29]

Figure 13. Fuel cell to be inserted into manifold.

Figure 14. Top-down exploded view of full assembly.

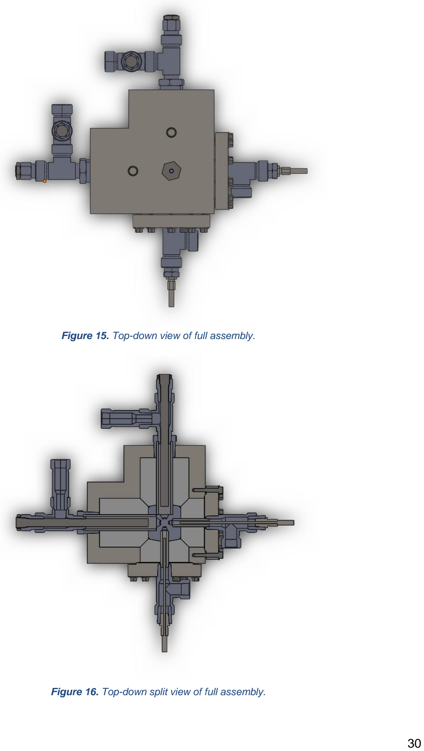
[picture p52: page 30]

Figure 15. Top-down view of full assembly.

Figure 16. Top-down split view of full assembly.

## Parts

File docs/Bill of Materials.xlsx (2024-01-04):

Product | Part Number | Company | Price per item | Quantity | Total | Link | Notes | Order Total
4" INSERTION CARTRIDGE HEATER 250W 120/240V STAINLESS STEEL NPT | TD50040KQ | Heating Elements Plus | $78.69 | 2 | $157.38 | https://www.heatingelementsplus.com/cartridge-heaters/standard-size-cartridge-heaters/1-2-inch-diameter-cartridge-heaters/cartridge-heater-stainless-steel-npt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 | Requires 3.5" unheated length extension | $2574.10
Conax Multi-wire Power Compression Seal Feedthrough ( PL ) | PL-18-A2-T | Conax Technologies | $120.00 | 2 | $240.00 | https://www.conaxtechnologies.com/product/conax-multi-wire-power-compression-seal-feedthrough-pl/
Ceramic Insulation Sheet for Furnaces Moldable, 1/4" Thick x 23" Wide x 2 Feet Long | 93615K18 | McMaster-Carr | $245.10 | 1 | $245.10 | https://www.mcmaster.com/93615k18
O-Ring - 3" ID High-Temperature Silicone, 0.125" Actual Width | 1169N303 | McMaster-Carr | $12.50 | 2 | $25.00 | https://www.mcmaster.com/1169N303 | Order with 3" ID
O-Ring 3.25" ID High-Temperature Silicone, 0.125" Actual Width | 1169N303 | McMaster-Carr | $12.50 | 2 | $25.00 | https://www.mcmaster.com/1169N303 | Order with 3.25" ID
Super-Corrosion-Resistant 316 Stainless Steel Hex Head Screws Serrated-Flange, 1/4"-20 Thread Size, 1-1/2" Long | 94302A105 | McMaster-Carr | $11.70 | 3 | $35.10 | https://www.mcmaster.com/94302A105
5/8" TUBE X 1/2" NPT MALE CONNECTOR | 100-10-8 | Lenz |  | 2 | $0.00 | https://lenzinc.com/product/100-10-8 | Lenz did not respond to quote requests
1 1/8"' TUBE X 1" NPT MALE CONNECTOR | 100-18-16 | Lenz |  | 2 | $0.00 | https://lenzinc.com/product/100-18-16 | Lenz did not respond to quote requests
Stainless Steel Pipe Fitting, Street Tee, 1/2 in. Female NPT x 1/2 in. Male NPT x 1/2 in. Female NPT | SS-8-ST | Swagelok | $66.90 | 6 | $401.40 | https://www.swagelok.com/en/catalog/Product/Detail?part=SS-8-ST
Stainless Steel Pipe Fitting, Reducing Bushing, 1/2 in. Male NPT x 1/4 in. Female NPT | SS-8-RB-4 | Swagelok | $12.50 | 2 | $25.00 | https://www.swagelok.com/en/catalog/Product/Detail?part=SS-8-RB-4
Stainless Steel Pipe Fitting, Reducing Bushing, 1/2 in. Male NPT x 3/8 in. Female NPT | SS-8-RB-6 | Swagelok | $12.90 | 2 | $25.80 | swagelok.com/en/catalog/Product/Detail?part=SS-8-RB-6
Stainless Steel Pipe Fitting, Reducing Bushing, 1 in. Male NPT x 1/2 in. Female NPT | SS-16-RB-8 | Swagelok | $26.00 | 2 | $52.00 | https://www.swagelok.com/en/catalog/Product/Detail?part=SS-16-RB-8
Stainless Steel Pipe Fitting, Reducing Bushing, 1/2 in. Male NPT x 1/8 in. Female NPT | SS-8-RB-2 | Swagelok | $12.10 | 2 | $24.20 | https://www.swagelok.com/en/catalog/Product/Detail?part=SS-8-RB-2
K type high temperature thermocouple with 1/4" NPT mounting adapter | WRNK-193 | Auber Instruments | $30.00 | 2 | $60.00 | https://www.auberins.com/index.php?main_page=product_info&cPath=20_3&products_id=650
PX2 Series Heavy Duty Pressure Transducer Sealed gage, 0 psi to 500 psi, 4.75 V to 5.25 V input, ratiometric: 5.0 Vdc 10 %Vs to 90 %Vs output, 1/8-27 NPT, Micro M12 (IEC 61076-2) | PX2BN2XX500PSAAX | Honeywell | $25.56 | 2 | $51.12 | https://www.newark.com/honeywell/px2bn2xx500psaax/pressure-transducer-500psi-1-8/dp/66W2309?CMP=AFC-ECIA
zirconia ceramic | 646-N | Aremco | 145$ for 4 lbs | 4 | $145.00 | https://www.aremco.com/potting-casting-materials/
Zirconia Tubes (8 mol% Y) | 31188 | Stanford Advanced Materials | 325*2 (for 1'' OD) 265*2 for .5" diameter | 4 | $1062.00 | https://www.samaterials.com/zirconium/533-zirconia-rod-tube.html | Tolerance is .5mm on all measurements
Nonporous Alumina Ceramic Tube 1" OD, 3/4" ID, 12" Long | 8746K551 | McMaster Carr | $131.98 | 2 | $263.96 | https://www.mcmaster.com/8746K551 | Not included in total
Nonporous Alumina Ceramic Tube 1/2" OD, 1/4" ID, 12" Long | 8746K19 | McMaster Carr | $35.40 | 2 | $70.80 | https://www.mcmaster.com/8746K19 | Not included in total

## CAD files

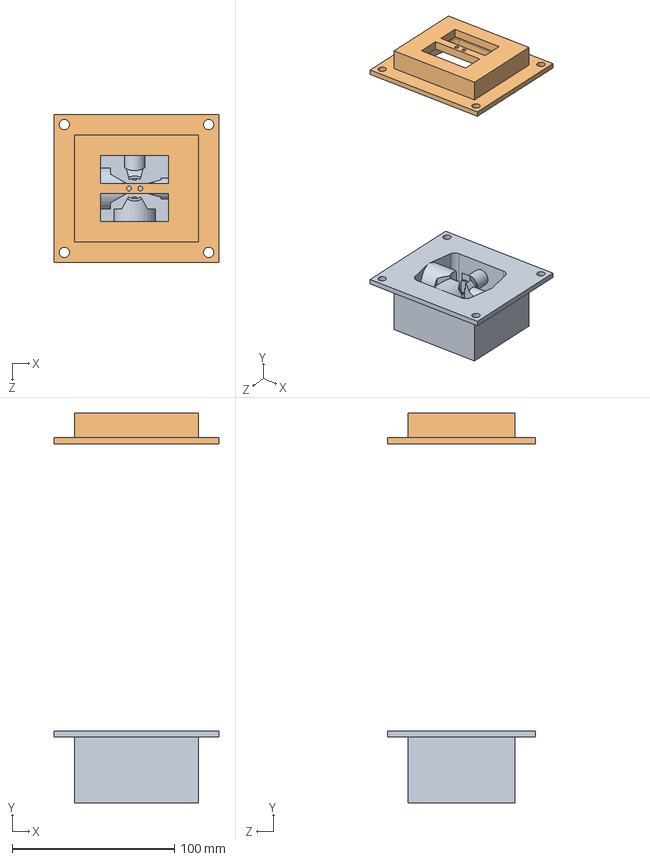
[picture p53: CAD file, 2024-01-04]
cad/Casted Manifold/Mold casting.SLDASM
101.6 x 240.2 x 91.4 mm
Mold part bottom
Mold part top

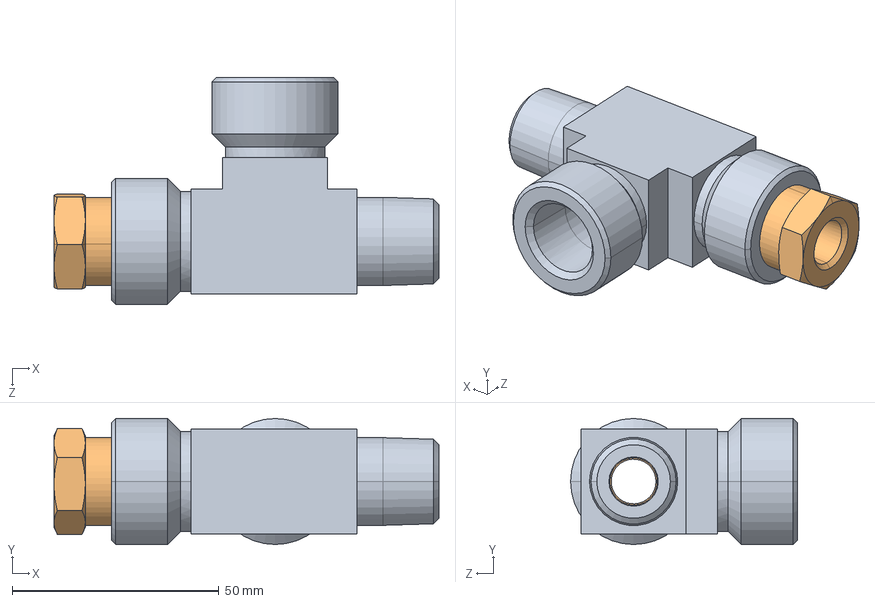
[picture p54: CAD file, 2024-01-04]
cad/Pressure Vessel/Seal_Exit.SLDASM
93.1 x 30.5 x 54.9 mm
SS-8-ST-SwagelokCompany--04-09-2020.stp
SS-8-RB-4-SwagelokCompany--04-09-2020

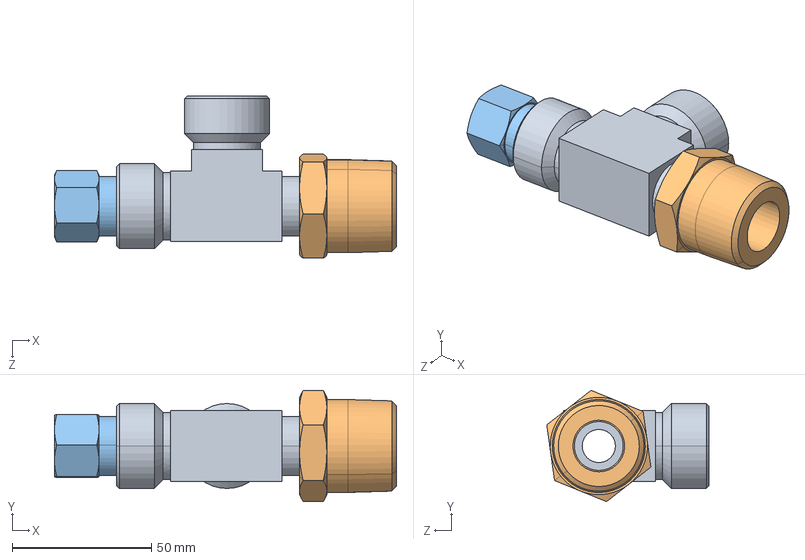
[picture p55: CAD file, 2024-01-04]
cad/Pressure Vessel/Enter_Seal.SLDASM
122.7 x 39.9 x 58.3 mm
SS-8-ST-SwagelokCompany--04-09-2020.stp
SS-16-RB-8-SwagelokCompany--04-09-2020.stp
SS-8-RB-6-SwagelokCompany--04-09-2020.stp

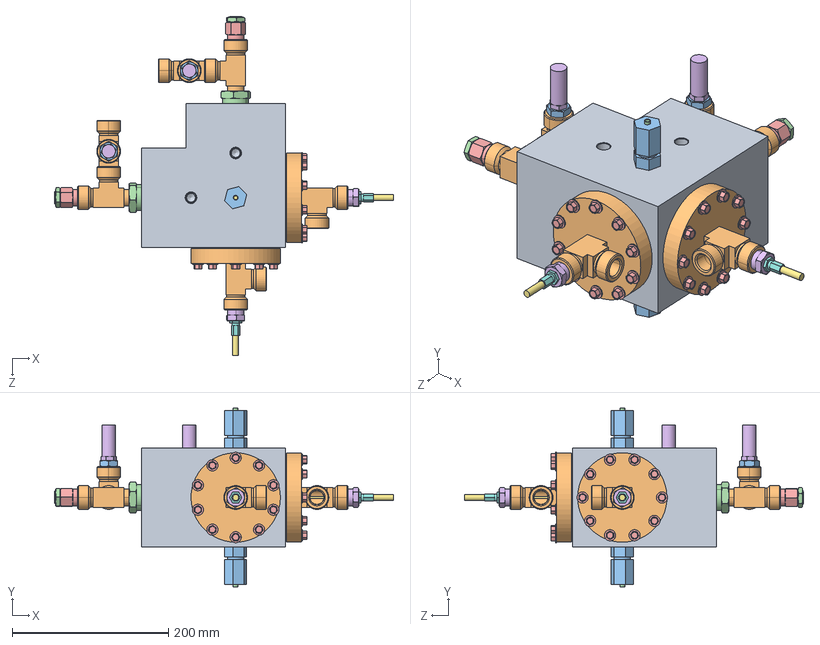
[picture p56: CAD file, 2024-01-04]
cad/Pressure Vessel/Pressure Manifold.SLDASM
433.6 x 228.9 x 433.6 mm
Pressure Vessel^Pressure Manifold
316L SS Plate^Pressure Manifold x 2
Cartridge Heater x 2
Cartridge Heater Nut^Pressure Manifold x 2
Alumina Tube 4.5in x 2
Alumina TubeSMALL x 2
Ceramic Insulation
Ceramic Insulation Corner
Ceramic InsulationSMALL Corner
Ceramic InsulationSMALL
Electrical Passthru^Pressure Manifold x 2
Teflon Sleeve^Pressure Manifold x 4
94302A105_SUPER-CORROSION-RST 316 SS HEX HEAD SCREWS x 20
Pressure Transducer^Pressure Manifold x 2
Manifold (3)
3in ID Rubber O-ring^Pressure Manifold x 2
3.25in ID Rubber O-ring^Pressure Manifold x 2
SS-8-ST-SwagelokCompany--04-09-2020.stp x 6
SS-8-RB-2-SwagelokCompany--04-14-2020.stp x 2
SS-16-RB-8-SwagelokCompany--04-09-2020.stp x 2
SS-8-RB-6-SwagelokCompany--04-09-2020.stp x 2
SS-8-RB-4-SwagelokCompany--04-09-2020 x 2
Type-K Thermocouple 0.25in NPT^Pressure Manifold x 2
Thermocouple Adapter^Pressure Manifold x 2

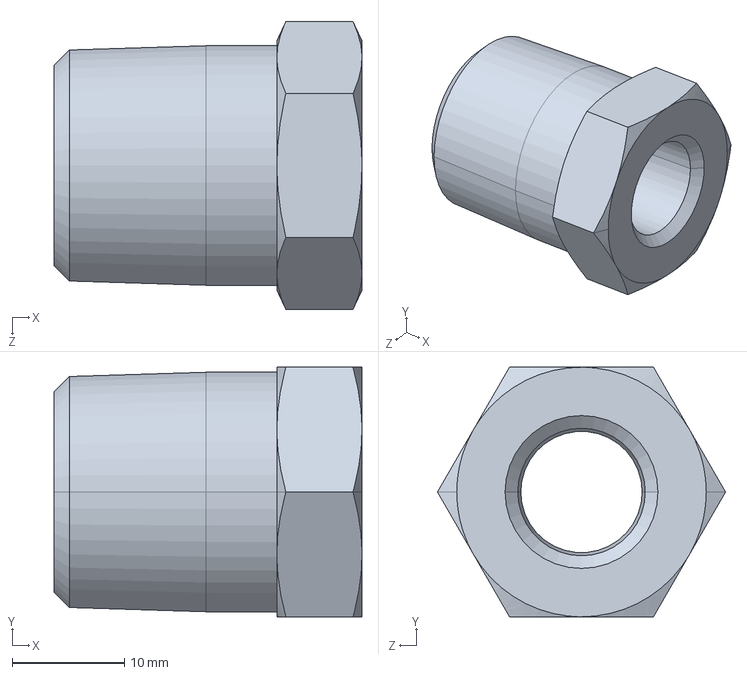
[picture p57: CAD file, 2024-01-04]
cad/Pressure Vessel/SS-8-RB-4-SwagelokCompany--04-09-2020.SLDPRT
27.4 x 22.2 x 25.7 mm

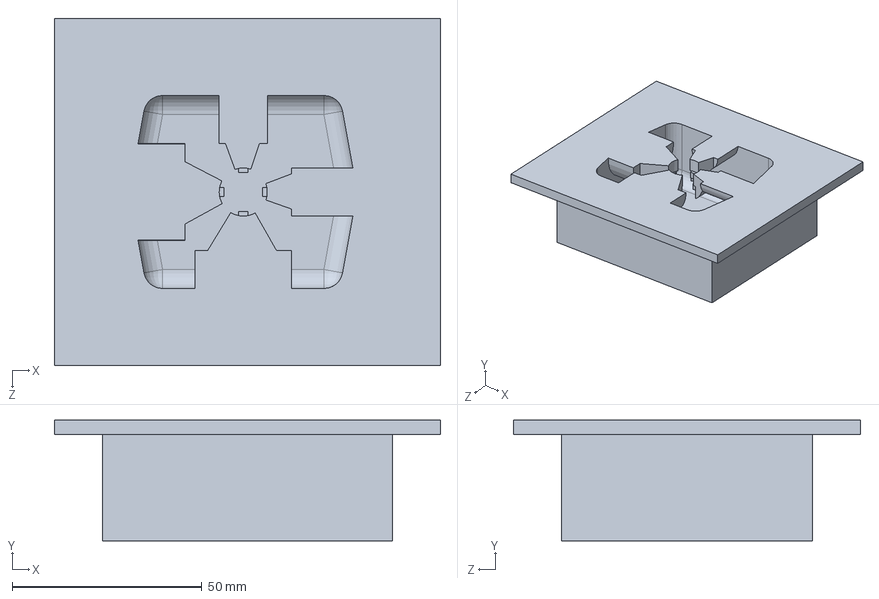
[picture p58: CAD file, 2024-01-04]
cad/Casted Manifold/Mold part bottom.SLDPRT
101.6 x 31.8 x 91.4 mm

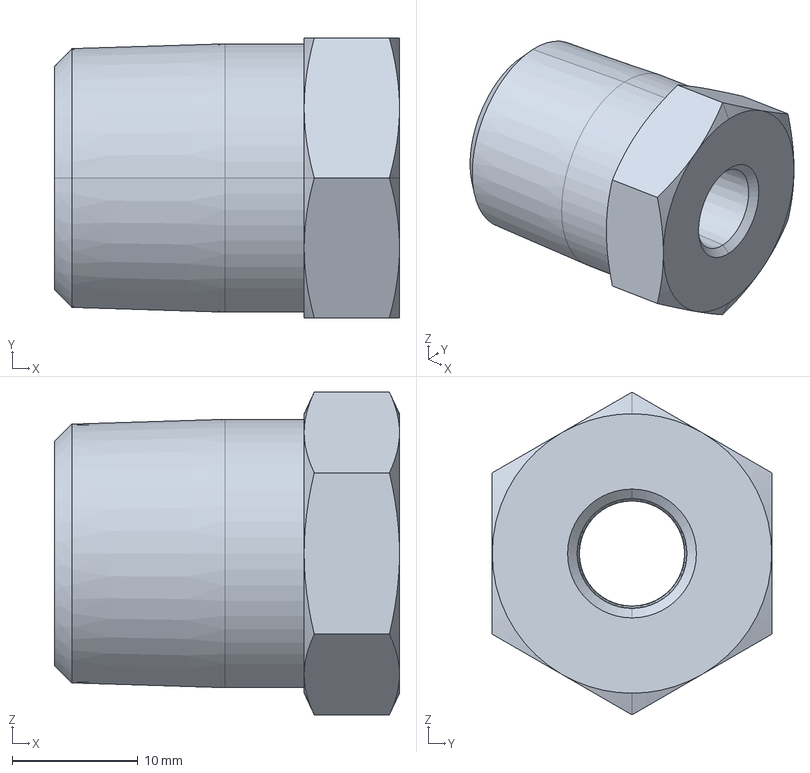
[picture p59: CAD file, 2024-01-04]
cad/Pressure Vessel/SS-8-RB-2-SwagelokCompany--04-14-2020.stp
27.4 x 22.2 x 25.7 mm

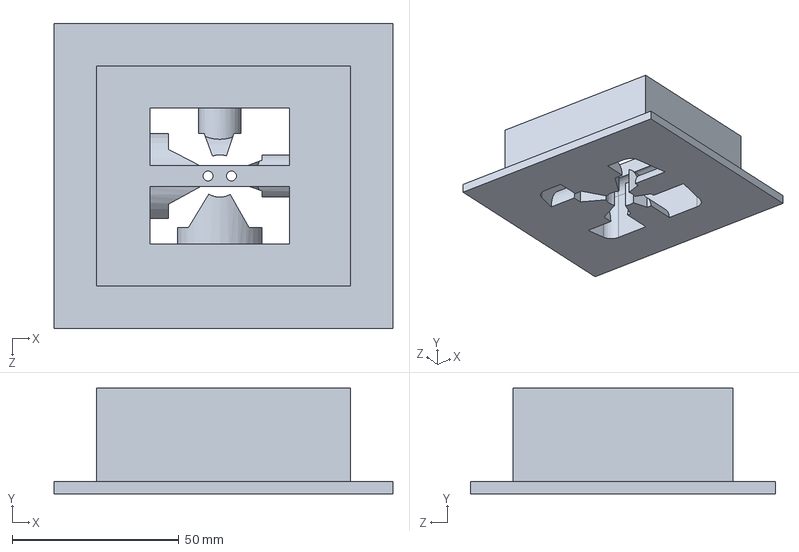
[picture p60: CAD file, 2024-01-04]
cad/Casted Manifold/Mold part top.SLDPRT
101.6 x 31.8 x 91.4 mm

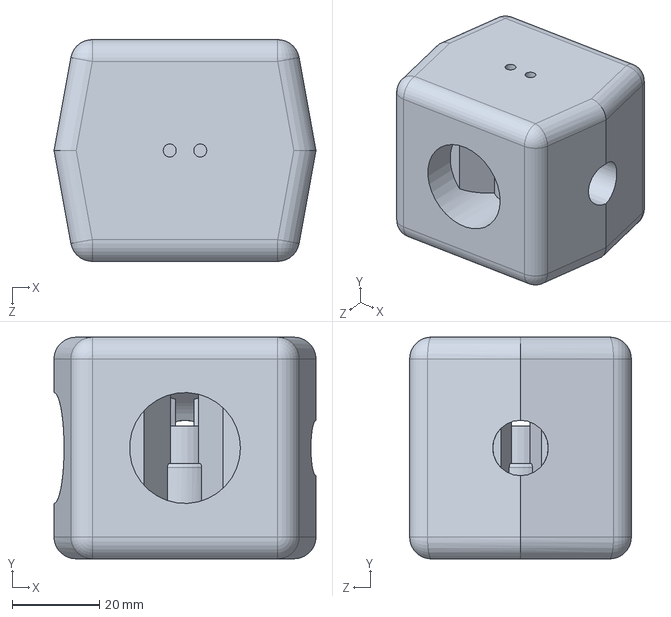
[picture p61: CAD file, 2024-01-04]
cad/Pressure Vessel/Manifold (3).SLDPRT
60.0 x 50.8 x 50.8 mm

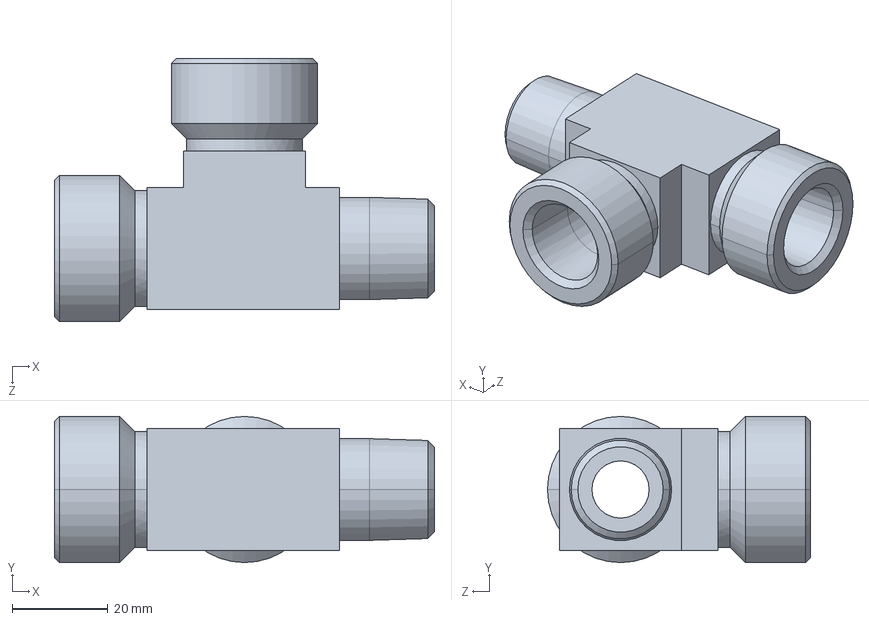
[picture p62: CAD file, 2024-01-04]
cad/Pressure Vessel/SS-8-ST-SwagelokCompany--04-09-2020.stp.SLDPRT
79.2 x 30.5 x 54.9 mm

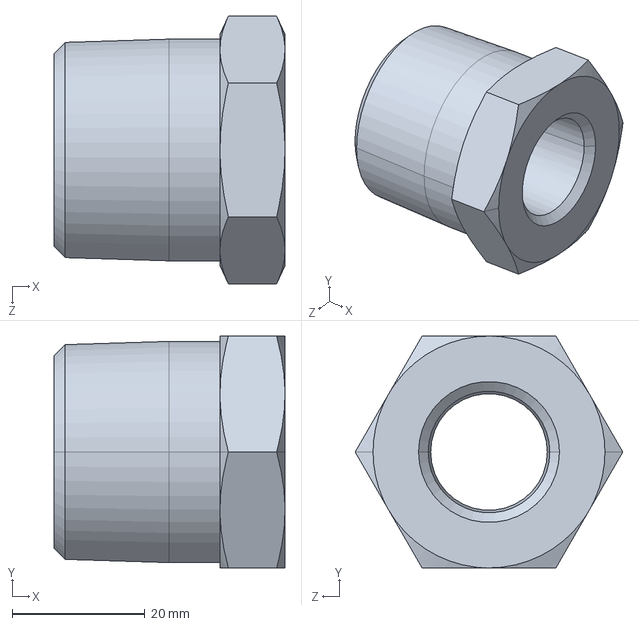
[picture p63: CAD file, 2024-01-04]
cad/Pressure Vessel/SS-16-RB-8-SwagelokCompany--04-09-2020.stp.SLDPRT
34.8 x 34.9 x 40.3 mm

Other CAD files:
cad/Casted Manifold/Manifold.SLDPRT
cad/Pressure Vessel/Ceramic InsulationSMALL.SLDPRT
cad/Pressure Vessel/Cartridge Heater.sldprt
cad/Pressure Vessel/Ceramic InsulationSMALL Corner.SLDPRT
cad/Pressure Vessel/Ceramic Insulation Corner.SLDPRT
cad/Pressure Vessel/Ceramic Insulation.sldprt
cad/Pressure Vessel/Alumina TubeSMALL.SLDPRT
cad/Pressure Vessel/316L SS Plate.sldprt
cad/Pressure Vessel/94302A105_SUPER-CORROSION-RST 316 SS HEX HEAD SCREWS.SLDPRT
cad/Pressure Vessel/Alumina Tube 4.5in.SLDPRT
cad/Pressure Vessel/Pressure Vessel.sldprt
cad/Pressure Vessel/SS-16-RB-8-SwagelokCompany--04-09-2020.stp
cad/Pressure Vessel/SS-8-RB-6-SwagelokCompany--04-09-2020.stp
cad/Pressure Vessel/SS-8-RB-6-SwagelokCompany--04-09-2020.stp.SLDPRT
cad/Pressure Vessel/SS-8-ST-SwagelokCompany--04-09-2020.stp
